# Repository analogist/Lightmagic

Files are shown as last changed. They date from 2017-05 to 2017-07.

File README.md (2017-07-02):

# Lightmagic
A safety-isolated dual-channel flexible audio and photodiode trigger for electrophysiological recording time synchronization and verification

## Design
The board has 2 inputs: a mono audio trigger (3.5mm / 1/8" jack, stereo combined) and a photodiode.

The photodiode is generally mounted to a screen or other photo synchronization trigger, and its sensitivity is adjustable with a trim pot. It's powered by a single regulated >5V low voltage source, usually a 9V battery. The audio jack is plugged into an audio synchronization trigger, and looks for any (3Hz highpassed) audio input higher than 0.7V. The audio half is powered by a mini-USB cable which may be hooked up to wall AC at some point, and the entire audio input is optically isolated from the photo trigger half of the board.

The output is an additional 3.5mm (1/8") audio jack with the L channel (tip) carrying the (rectified, amplified, isolated) audio trigger signal and the R channel (ring) carrying the (amplified) photodiode signal. Both channel should swing from 0 (off) - 2V (trigger on) with the standard BOM items.

The design allows for this board to be "trigger glue" between a psychophysical presentation (audio or on-screen stimuli) and electrophysiological recording systems when sub-millisecond synchronization is required, such as for neurostimulation. Note that output voltages are still in the 2V range; this should be further reduced as close as possible to the recording system via passive voltage dividers down to safe voltages and currents (hopefully <50μA for all failure conditions) for in-vivo recordings.

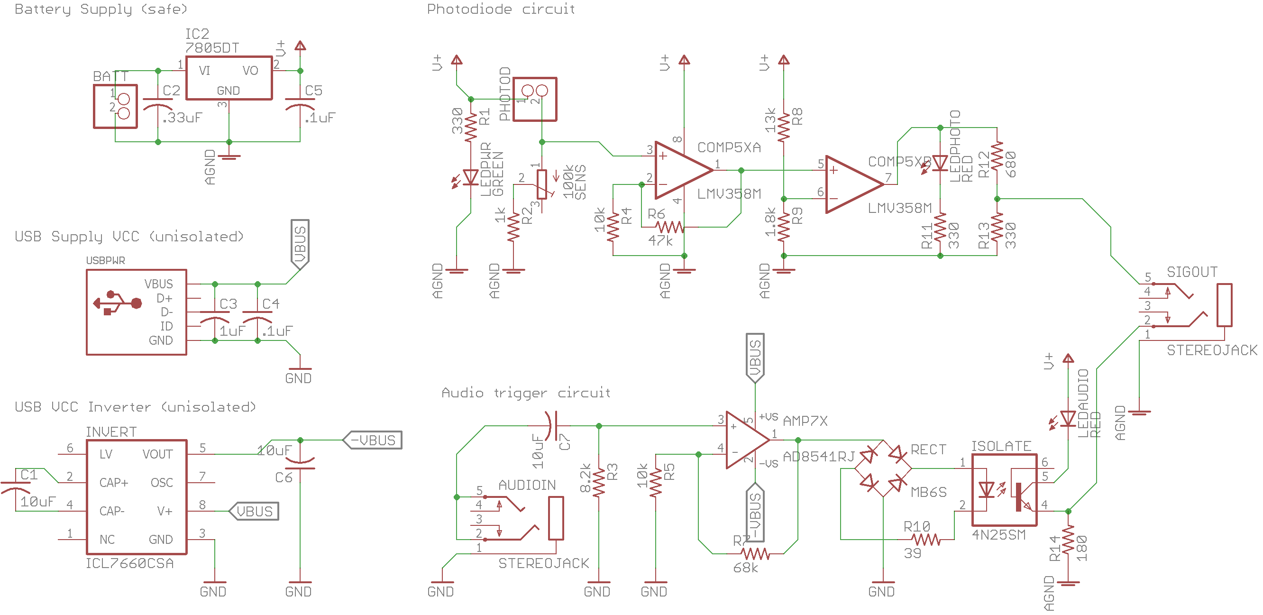
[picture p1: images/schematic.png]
Schematic

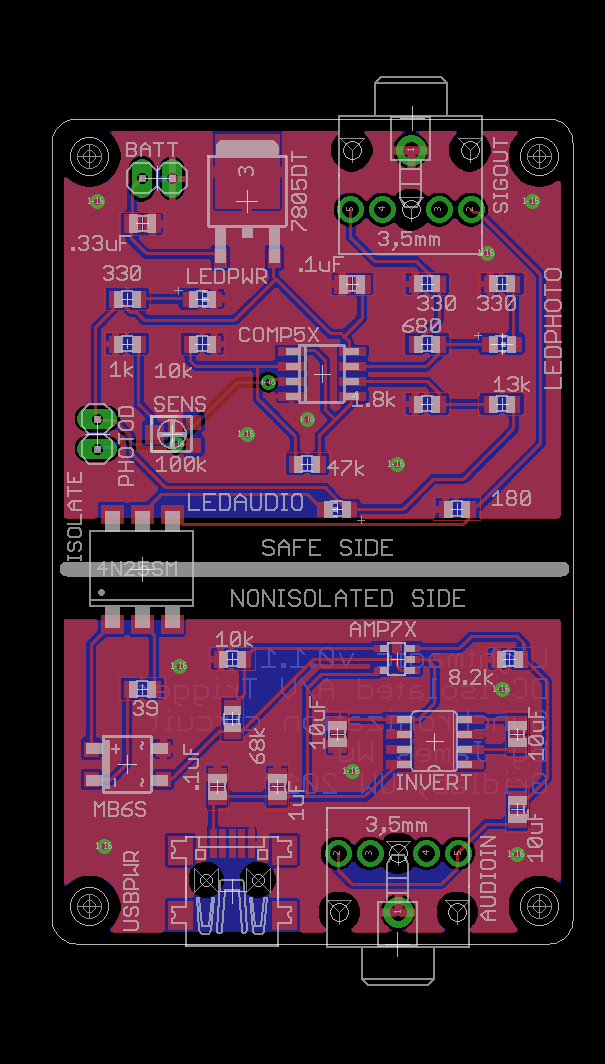
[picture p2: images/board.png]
Board


## Files

The source Eagle CAD files are in the `eagle` directory.
The OSH Park-compatible `ger` and `xln` files can be found in the `gerber` directory. Zipping it will allow for manufacture.

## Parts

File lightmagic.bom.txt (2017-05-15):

Part     Value      Device          Package      Description                                                                   MF                      MPN                OC_FARNELL OC_NEWARK
AMP7X    AD8541RJ   AD8541RJ        SOT23-5      General-Purpose CMOS Rail-to-Rail Amplifiers                                                          AD8541ARTZ-R2      1464963    28X4209  
AUDIOIN  STEREOJACK STEREOJACK      STX3100      MIC/HEADPHONE JACK                                                            SWITCHCRAFT             35RAPC4BHN2                   96F9607  
BATT                PINHD-1X2       1X02         PIN HEADER                                                                    TYCO ELECTRONICS        640456-2                      90F4250  
C1       10uF       C-USC0805       C0805        CAPACITOR, American symbol                                                                            GRT21BR61E106KE13L            01AC8983 
C2       .33uF      C-USC0805       C0805        CAPACITOR, American symbol                                                                            MC0805B334K500CT              06X6218  
C3       1uF        C-USC0805       C0805        CAPACITOR, American symbol                                                                            C0805X104K3RAC3316            01AC1593 
C4       .1uF       C-USC0805       C0805        CAPACITOR, American symbol                                                                            0805YC104KAT2A                05AC9650 
C5       .1uF       C-USC0805       C0805        CAPACITOR, American symbol                                                                            0805YC104KAT2A                05AC9650 
C6       10uF       C-USC0805       C0805        CAPACITOR, American symbol                                                                            GRT21BR61E106KE13L            01AC8983 
C7       10uF       C-USC0805       C0805        CAPACITOR, American symbol                                                                            GRT21BR61E106KE13L            01AC8983 
COMP5X   LMV358M    LMV358M         SO08         Dual General Purpose, Low Voltage, Rail-to-Rail Output Operational Amplifiers                         LMV358M                       97K3153  
IC2      7805DT     7805DT          TO252        Positive VOLTAGE REGULATOR                                                    ON SEMICONDUCTOR        MC7805CDTG                    71J5739  
INVERT   ICL7660CSA ICL7660CSA      SO08         VOLTAGE CONVERTER                                                             NATIONAL SEMICONDUCTOR  LMC7660IM/NOPB     9724710    41K2738  
ISOLATE  4N25SM     4N25SM          DIL6-SMD     General Purpose 6-Pin Phototransistor Optocouplers                                                    4N25-300E          1021152    13M5766  
LEDAUDIO RED        LEDCHIP-LED0805 CHIP-LED0805 LED                                                                                                   QTLP630C7TR                   01AC7976 
LEDPHOTO RED        LEDCHIP-LED0805 CHIP-LED0805 LED                                                                                                   QTLP630C7TR                   01AC7976 
LEDPWR   GREEN      LEDCHIP-LED0805 CHIP-LED0805 LED                                                                                                   QTLP630C7TR                   01AC7976 
PHOTOD              PINHD-1X2       1X02         PIN HEADER                                                                    TYCO ELECTRONICS        640456-2                      90F4250  
R1       330        R-US_R0805      R0805        RESISTOR, American symbol                                                                             ERJ-6ENF3300V                 90W3413  
R2       1k         R-US_R0805      R0805        RESISTOR, American symbol                                                                             ERJ-6ENF12R0V                 64R5373  
R3       8.2k       R-US_R0805      R0805        RESISTOR, American symbol                                                     Multicomp Passives      MC01W080518K2                 58K4911  
R4       10k        R-US_R0805      R0805        RESISTOR, American symbol                                                     VISHAY/DALE             CRCW080510K0FKTA              05F1511  
R5       10k        R-US_R0805      R0805        RESISTOR, American symbol                                                     VISHAY/DALE             CRCW080510K0FKTA              05F1511  
R6       47k        R-US_R0805      R0805        RESISTOR, American symbol                                                     VISHAY/DALE             CRCW080547K0FKEA              42K4553  
R7       68k        R-US_R0805      R0805        RESISTOR, American symbol                                                     VISHAY/DALE             CRCW080568K0FKEA              53K0428  
R8       13k        R-US_R0805      R0805        RESISTOR, American symbol                                                     VISHAY/DALE             CRCW080513K0FKEA              42K4278  
R9       1.8k       R-US_R0805      R0805        RESISTOR, American symbol                                                     VISHAY/DALE             CRCW08051K80FKEA              42K4228  
R10      39         R-US_R0805      R0805        RESISTOR, American symbol                                                                             ERJ-6GEYJ390V                 53W4957  
R11      330        R-US_R0805      R0805        RESISTOR, American symbol                                                                             ERJ-6ENF3300V                 90W3413  
R12      680        R-US_R0805      R0805        RESISTOR, American symbol                                                                             ERA-6AEB681V                  08N2184  
R13      330        R-US_R0805      R0805        RESISTOR, American symbol                                                                             ERJ-6ENF3300V                 90W3413  
R14      180        R-US_R0805      R0805        RESISTOR, American symbol                                                     VISHAY/DALE             CRCW0805180RJNEA              01H7775  
RECT     MB6S       MB6S            SOIC-4       Bridge Rectifier                                                              FAIRCHILD SEMICONDUCTOR MB6S                          58K1814  
SENS     100k       TRIMPOTTC33X    TC33X        SMT trimmer potentiometer part number TC33X                                                           CRCW0805100KJNEA              04M8142  
SIGOUT   STEREOJACK STEREOJACK      STX3100      MIC/HEADPHONE JACK                                                            SWITCHCRAFT             35RAPC4BHN2                   96F9607  
USBPWR              USBMINIB        USB-MINIB    USB Connectors                                                                                        1734035-1                     16M2760

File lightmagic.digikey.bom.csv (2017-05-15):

Index | Quantity | Part Number | Manufacturer Part Number | Description | Customer Reference | Backorder | Unit Price | Extended Price
1 | 3 | MC7805ECDTXCT-ND | MC7805ECDTX | IC REG LDO 5V 1A TO252-3 | IC2 | 0 | 0.75000 | $2.25
2 | 3 | 490-3327-1-ND | GRM219R71H334KA88D | CAP CER 0.33UF 50V X7R 0805 | C2 | 0 | 0.32000 | $0.96
3 | 10 | 478-1395-1-ND | 08055C104KAT2A | CAP CER 0.1UF 50V X7R 0805 | C4C5 | 0 | 0.03100 | $0.31
4 | 3 | LMC7660IMX/NOPBCT-ND | LMC7660IMX/NOPB | IC REG SWTCHD CAP INV 8SOIC | INVERT | 0 | 0.96000 | $2.88
5 | 3 | 160-1910-1-ND | 4N25S-TA1 | OPTOISO 2.5KV TRANS W/BASE 6SMD | ISOLATE | 0 | 0.59000 | $1.77
6 | 10 | RMCF0805JT8K20CT-ND | RMCF0805JT8K20 | RES SMD 8.2K OHM 5% 1/8W 0805 | R3 | 0 | 0.01600 | $0.16
7 | 10 | RMCF0805JT1K80CT-ND | RMCF0805JT1K80 | RES SMD 1.8K OHM 5% 1/8W 0805 | R9 | 0 | 0.01600 | $0.16
8 | 10 | RMCF0805JT47K0CT-ND | RMCF0805JT47K0 | RES SMD 47K OHM 5% 1/8W 0805 | R6 | 0 | 0.01600 | $0.16
9 | 10 | 311-13KARCT-ND | RC0805JR-0713KL | RES SMD 13K OHM 5% 1/8W 0805 | R8 | 0 | 0.01800 | $0.18
10 | 10 | RMCF0805JT680RCT-ND | RMCF0805JT680R | RES SMD 680 OHM 5% 1/8W 0805 | R12 | 0 | 0.01600 | $0.16
11 | 10 | RMCF0805JT180RCT-ND | RMCF0805JT180R | RES SMD 180 OHM 5% 1/8W 0805 | R14 | 0 | 0.01600 | $0.16
12 | 3 | MB6SCT-ND | MB6S | IC RECT BRIDGE 0.5A 600V 4SOIC | RECT | 0 | 0.38000 | $1.14
13 | 3 | 151-1206-1-ND | 690-005-299-043 | CONN MINI USB RCPT RA TYPE B SMD | USBMINIB | 0 | 0.54000 | $1.62
14 | 6 | CP1-3523N-ND | SJ1-3523N | CONN JACK STEREO 3.5MM R/A | AUDIOINSIGOUT | 0 | 0.74000 | $4.44
15 | 10 | 311-10KARCT-ND | RC0805JR-0710KL | RES SMD 10K OHM 5% 1/8W 0805 | R4R5 | 0 | 0.01800 | $0.18
16 | 3 | AD8541ARTZ-REEL7CT-ND | AD8541ARTZ-REEL7 | IC OPAMP GP 1MHZ RRO SOT23-5 | AMP7X | 0 | 0.89000 | $2.67
17 | 10 | RMCF0805JT330RCT-ND | RMCF0805JT330R | RES SMD 330 OHM 5% 1/8W 0805 | R1R11R13 | 0 | 0.01600 | $0.16
18 | 3 | 475-1410-1-ND | LG R971-KN-1 | LED GREEN DIFFUSED 0805 SMD | LEDPWR | 0 | 0.25000 | $0.75
19 | 6 | 475-1278-1-ND | LS R976-NR-1 | LED RED DIFFUSED 0805 SMD | LEDAUDIOPHOTO | 0 | 0.26000 | $1.56
20 | 3 | 497-4945-1-ND | LMV358IDT | IC OPAMP GP 1.3MHZ RRO 8SO | IC1 | 0 | 0.45000 | $1.35
21 | 10 | RMCF0805JT68K0CT-ND | RMCF0805JT68K0 | RES SMD 68K OHM 5% 1/8W 0805 | R7 | 0 | 0.01600 | $0.16
22 | 3 | TC33X-104ECT-ND | TC33X-2-104E | TRIMMER 100K OHM 0.1W SMD | SENS | 0 | 0.28000 | $0.84
23 | 10 | RMCF0805JT1K00CT-ND | RMCF0805JT1K00 | RES SMD 1K OHM 5% 1/8W 0805 | R2 | 0 | 0.01600 | $0.16
24 | 10 | 399-4925-1-ND | C0805C106K8PACTU | CAP CER 10UF 10V X5R 0805 | C1C6C7 | 0 | 0.08900 | $0.89
25 | 6 | A1921-ND | 640456-2 | CONN HEADER VERT 2POS .100 TIN | BATTPHOTOD | 0 | 0.12000 | $0.72
26 | 6 | A30978-ND | 3-640441-2 | CONN RECEPT 2POS 24AWG MTA100 | BATTPHOTOD | 0 | 0.18000 | $1.08
27 | 10 | RMCF0805JT39R0CT-ND | RMCF0805JT39R0 | RES SMD 39 OHM 5% 1/8W 0805 | R10 | 0 | 0.01600 | $0.16
28 | 3 | 311-1365-1-ND | CC0805KKX7R7BB105 | CAP CER 1UF 16V X7R 0805 | C3 | 0 | 0.10000 | $0.30
29 | 3 | PDB-C156-ND | PHOTODIODE BLUE 8.02MM SQ CLEAR | PHOTODIODE | 3 | 0 | 1.68000 | $5.04

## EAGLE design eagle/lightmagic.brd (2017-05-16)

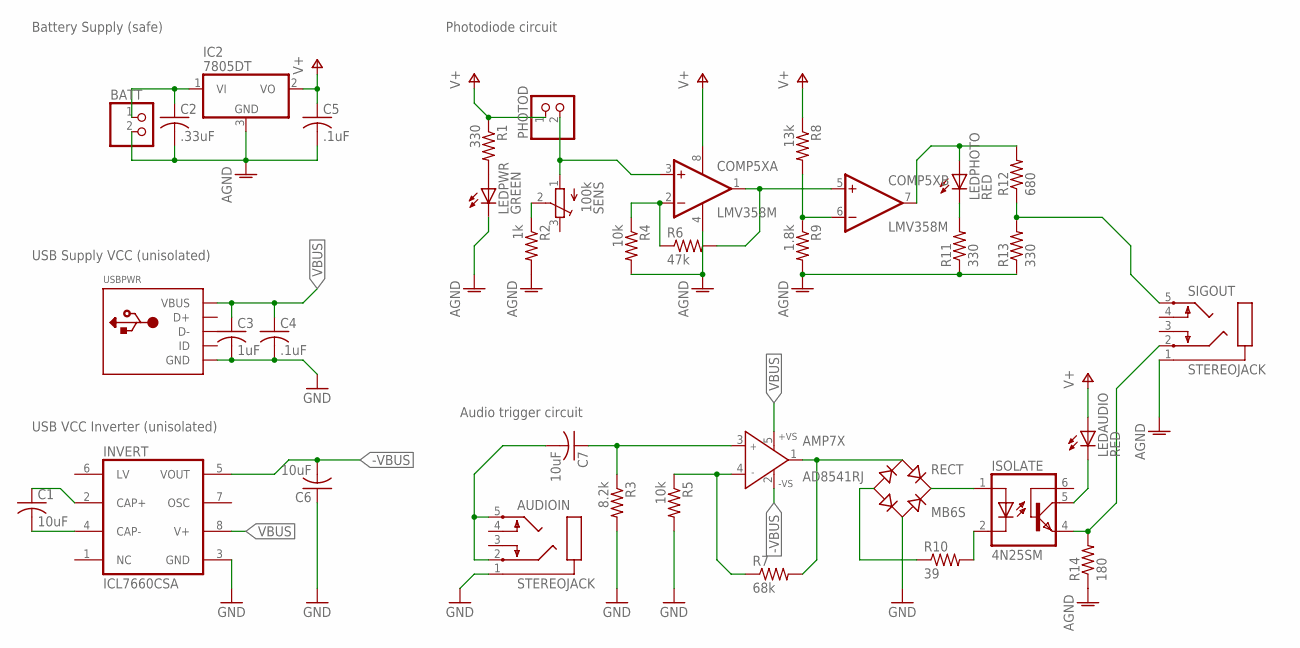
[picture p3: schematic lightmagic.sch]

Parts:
AMP7X: AD8541RJ; SOT23-5; MPN AD8541ARTZ-R2
AUDIOIN: STEREOJACK; STX3100; MPN 35RAPC4BHN2
BATT: PINHD-1X2; 1X02; MPN 640456-2
C1, C6, C7: 10uF; C0805; MPN GRT21BR61E106KE13L
C2: .33uF; C0805; MPN MC0805B334K500CT
C3: 1uF; C0805; MPN C0805X104K3RAC3316
C4, C5: .1uF; C0805; MPN 0805YC104KAT2A
COMP5X: LMV358M; SO08; MPN LMV358M
IC2: 7805DT; TO252; MPN MC7805CDTG
INVERT: ICL7660CSA; SO08; MPN LMC7660IM/NOPB
ISOLATE: 4N25SM; DIL6-SMD; MPN 4N25-300E
LEDAUDIO: RED; CHIP-LED0805; MPN QTLP630C7TR
LEDPHOTO: RED; CHIP-LED0805; MPN QTLP630C7TR
LEDPWR: GREEN; CHIP-LED0805; MPN QTLP630C7TR
PHOTOD: PINHD-1X2; 1X02; MPN 640456-2
R1, R11, R13: 330; R0805; MPN ERJ-6ENF3300V
R2: 1k; R0805; MPN ERJ-6ENF12R0V
R3: 8.2k; R0805; MPN MC01W080518K2
R4, R5: 10k; R0805; MPN CRCW080510K0FKTA
R6: 47k; R0805; MPN CRCW080547K0FKEA
R7: 68k; R0805; MPN CRCW080568K0FKEA
R8: 13k; R0805; MPN CRCW080513K0FKEA
R9: 1.8k; R0805; MPN CRCW08051K80FKEA
R10: 39; R0805; MPN ERJ-6GEYJ390V
R12: 680; R0805; MPN ERA-6AEB681V
R14: 180; R0805; MPN CRCW0805180RJNEA
RECT: MB6S; SOIC-4; MPN MB6S
SENS: 100k; TC33X; MPN CRCW0805100KJNEA
SIGOUT: STEREOJACK; STX3100; MPN 35RAPC4BHN2
USBPWR: USBMINIB; USB-MINIB; MPN 1734035-1

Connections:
-VBUS: AMP7X.2 (-VS), C6.2, INVERT.5 (VOUT)
AGND: BATT.2, C2.2, C5.2, COMP5X.4 (V-), IC2.3 (GND), LEDPWR.C, R2.2, R4.2, R9.2, R11.1, R13.1, R14.1, SIGOUT.1
GND: AUDIOIN.1, C3.2, C4.2, C6.1, INVERT.3 (GND), R3.2, R5.2, RECT.~2 (AC2), USBPWR.GND
unnamed: AMP7X.4 (IN-), R5.1, R7.1
unnamed: C1.1, INVERT.2 (CAP+)
unnamed: C1.2, INVERT.4 (CAP-)
unnamed: AUDIOIN.2, AUDIOIN.5, C7.2
unnamed: AMP7X.3 (IN+), C7.1, R3.1
unnamed: AMP7X.1 (OUT), R7.2, RECT.~1 (AC1)
unnamed: ISOLATE.1 (A), RECT.+
unnamed: ISOLATE.2 (C), R10.2
unnamed: R10.1, RECT.-
unnamed: BATT.1, C2.1, IC2.1 (VI)
unnamed: R2.1, SENS.2 (S)
unnamed: LEDPWR.A, R1.2
unnamed: COMP5X.3 (+IN), PHOTOD.2, SENS.1 (A)
unnamed: COMP5X.2 (-IN), R4.1, R6.1
unnamed: COMP5X.1 (OUT), COMP5X.5 (+IN), R6.2
unnamed: COMP5X.6 (-IN), R8.2, R9.1
unnamed: ISOLATE.4 (EMI), R14.2, SIGOUT.2
unnamed: ISOLATE.5 (COL), LEDAUDIO.C
unnamed: LEDPHOTO.C, R11.2
unnamed: R12.1, R13.2, SIGOUT.5
unnamed: COMP5X.7 (OUT), LEDPHOTO.A, R12.2
V+: C5.1, COMP5X.8 (V+), IC2.2 (VO), LEDAUDIO.A, PHOTOD.1, R1.1, R8.1
VBUS: AMP7X.5 (+VS), C3.1, C4.1, INVERT.8 (V+), USBPWR.VBUS

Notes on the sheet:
Battery Supply (safe)
USB VCC Inverter (unisolated)
USB Supply VCC (unisolated)
Photodiode circuit
Audio trigger circuit

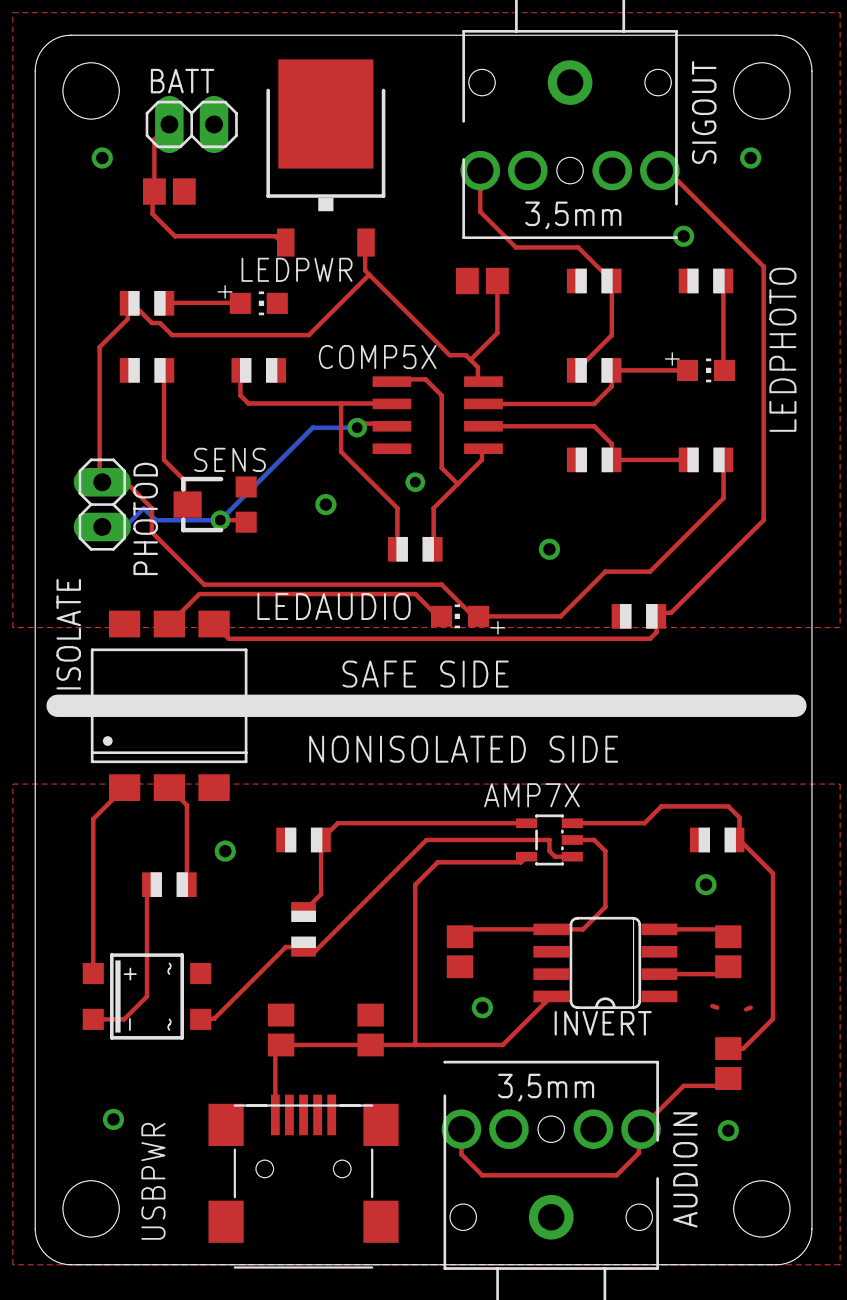
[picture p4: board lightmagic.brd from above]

Board: 2 copper layers, 44.1 x 69.8 mm, 36 parts (0 on the bottom side), 26 nets.

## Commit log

2017-05-15 Lightmagic v0.1, first prototype
    [lightmagic.brd, lightmagic.drills.xln, lightmagic.sch]
2017-05-15 v0.1.1, fixed some paths and positions
    [lightmagic.brd, lightmagic.drills.xln]
2017-05-15 update parts list, miter corners
    [lightmagic.brd, lightmagic.sch]
2017-05-15 add BOM, order, images
    [lightmagic.digikey.bom.csv]
2017-05-16 reroute audio side
    [lightmagic.brd, lightmagic.drills.xln]
